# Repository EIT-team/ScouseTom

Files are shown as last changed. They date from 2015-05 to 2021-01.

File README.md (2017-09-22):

# ScouseTom EIT System
The __ScouseTom__ is versatile Electrical Impedance Tomography (EIT) system. It comprises a commercial current source [Keithley 6221](http://www.tek.com/keithley-low-level-sensitive-and-specialty-instruments/keithley-ultra-sensitive-current-sources-seri) and EEG amplifiers e.g. [Biosemi](http://www.biosemi.com/) or the [actiCHamp](http://www.brainvision.com/actichamp.html0), alongside custom switching/control circuitry and software.

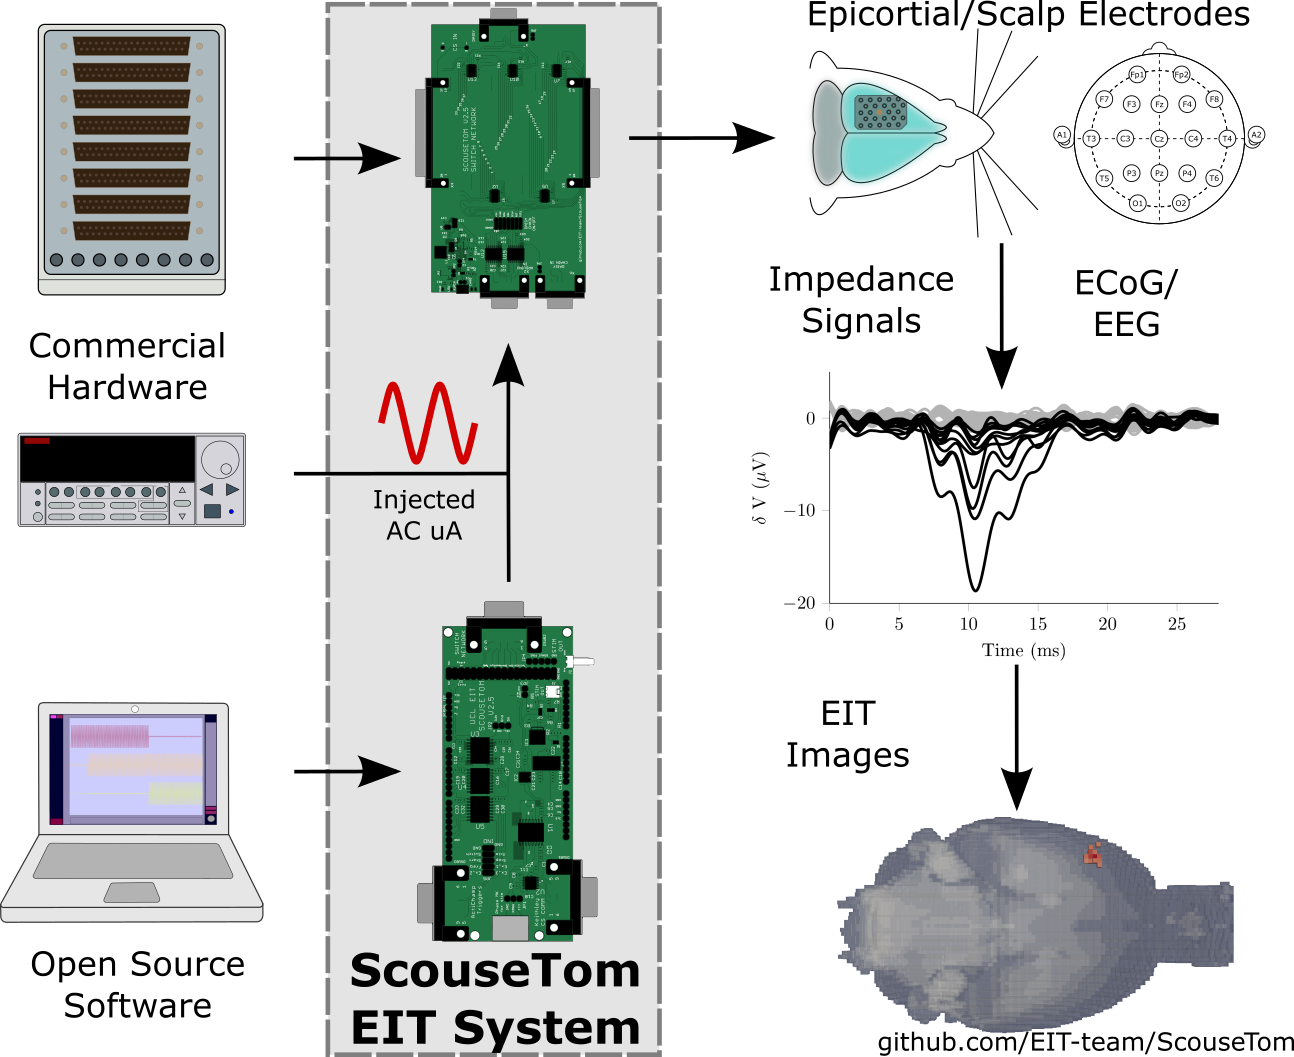
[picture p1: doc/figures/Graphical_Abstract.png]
ScouseTom System Overview


## Making a ScouseTom
If you are interested in making a ScouseTom EIT system, please create an __issue__ in the repo or email us, we would love to help you!

__Checklist__
- [Keithley 6221](http://www.tek.com/keithley-low-level-sensitive-and-specialty-instruments/keithley-ultra-sensitive-current-sources-seri) Current source
- EEG system with sufficient bandwidth. The [Biosemi](http://www.biosemi.com/) and  [actiCHamp](http://www.brainvision.com/actichamp.html0) have been used so far, and likely the [gtec](http://www.gtec.at/) or the [Open-Ephys](http://www.open-ephys.org/) will work too
- Matlab - needed for [processing](https://github.com/EIT-team/Load_data) anyway. Control the system using the Matlab code [here](./src/matlab/)
- [Arduino Due](https://www.arduino.cc/en/Main/arduinoBoardDue) For the controller
- [Arduino Switch Board](./src/schematics/Ard_Shield) This controls the current source and the timing of switching current injection pairs
- [Switch Network](./src/schematics/ScouseTom_SwitchNetwork) At least one, each for 37 channels. This connects the current source to the EEG system and the electrodes

### Citing this work
Please cite the journal article found [here](http://dx.doi.org/10.3390/s17020280)

```
Avery, J., Dowrick, T., Faulkner, M., Goren, N. and Holder, D., 2017.
A Versatile and Reproducible Multi-Frequency Electrical Impedance Tomography System.
Sensors, 17(2), p.280.
```

### Processing the data
To process the data you collect with this system, use the code found in [this repo](https://github.com/EIT-team/Load_data)

### Creating EIT images
Requires a forward model, generated by the code [here](https://github.com/EIT-team/PEITS), and the reconstruction code [here](https://github.com/EIT-team/Reconstruction) to create the images

## Keithley settings
Set on the front panel under `comm`, change `BAUD` to `57.2k` and `Terminator` to `<CR+LF>`

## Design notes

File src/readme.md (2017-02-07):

# ScouseTom Source Files
---

## Arduino
Firmware for the Arduino controllers

## Labview
Measurement of stimulator voltage, used in calibration

## Matlab
PC software for controlling the system via USB

## Schematics
Contains all the schematics in Eagle format for the two PCBs - Arduino Shield, and Switch Network. Also contains resistor phantoms, and other misc. phantoms useful in experiments.

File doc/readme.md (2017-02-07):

# Useful Documentation
This folder contains reference material for hardware, and software used in making the ScouseTom. It also contains 3D models for cases and electrode holders.

- __ActiChamp Holder__ Boxes to hold the active electrodes of the ActiChamp systems
- __Arduino__ Reference for pinouts etc. for Uno and Due
- __BioSemi__ BioSemi Active Two Reference material and software
- __case__ 3D printable cases for both ScouseTom boards - the arduino+shield, and the switch boards
- __Eagle__ Design Rule checks and Cam jobs for EagleCad
- __figures__ Figures of ScouseTom components, useful for Documentation
- __Keithley__ Manuals for Keithley 6221 Current source, as well as guide to upgrading firmware
- __PCB__ Example BOM etc. for ordering boards

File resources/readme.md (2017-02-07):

# Example files

## data
Data collected on resistor phantoms, used for getting system specs for paper.

## protocols
Protocol files which can be used for creating the `ExpSetup` structure

## stim_calibration
Example outputs from stimulator calibration - potentiometer settings for given stimulator voltages. These are the ones used to create the default settings (no one calibrates it anyways...)

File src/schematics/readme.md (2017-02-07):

# Schematics
The schematics needed to create a ScouseTom system and custom electrode boards are all here. All files were created in Eaglecad, and the gerber files are also saved. Where relevant, BOM and pick and place data are included.

- __ _Superseded __ - Old files of historical interest
- __Ard Shield__ - Shield for the Arduino Due which controls the ScouseTom System
- __Debug_Phantom__ A simple resistor phantom, used to quickly check the system is functional, as opposed to calibration
- __Dsub_Croc_Connector__ A breakout for a 37-Way Dsub connector to make it easy to solder crocdile clips to it - to connect to tanks etc.
- __Flexible_Electrode_Connector__ Connector blocks for the flexible electrodes used in epicortical studies
- __Mayo_Phantom__ Resistor Phantom matching epicortical voltages, with three switchable impedances. Used to compare hardware for EP studies
- __Parallel_CS__ Simple current source
- __ScouseTom_SwitchNetwork__ Switch network used in ScouseTom system - 37 channels, and can be daisy chained

## The ones you need to  make a ScouseTom System

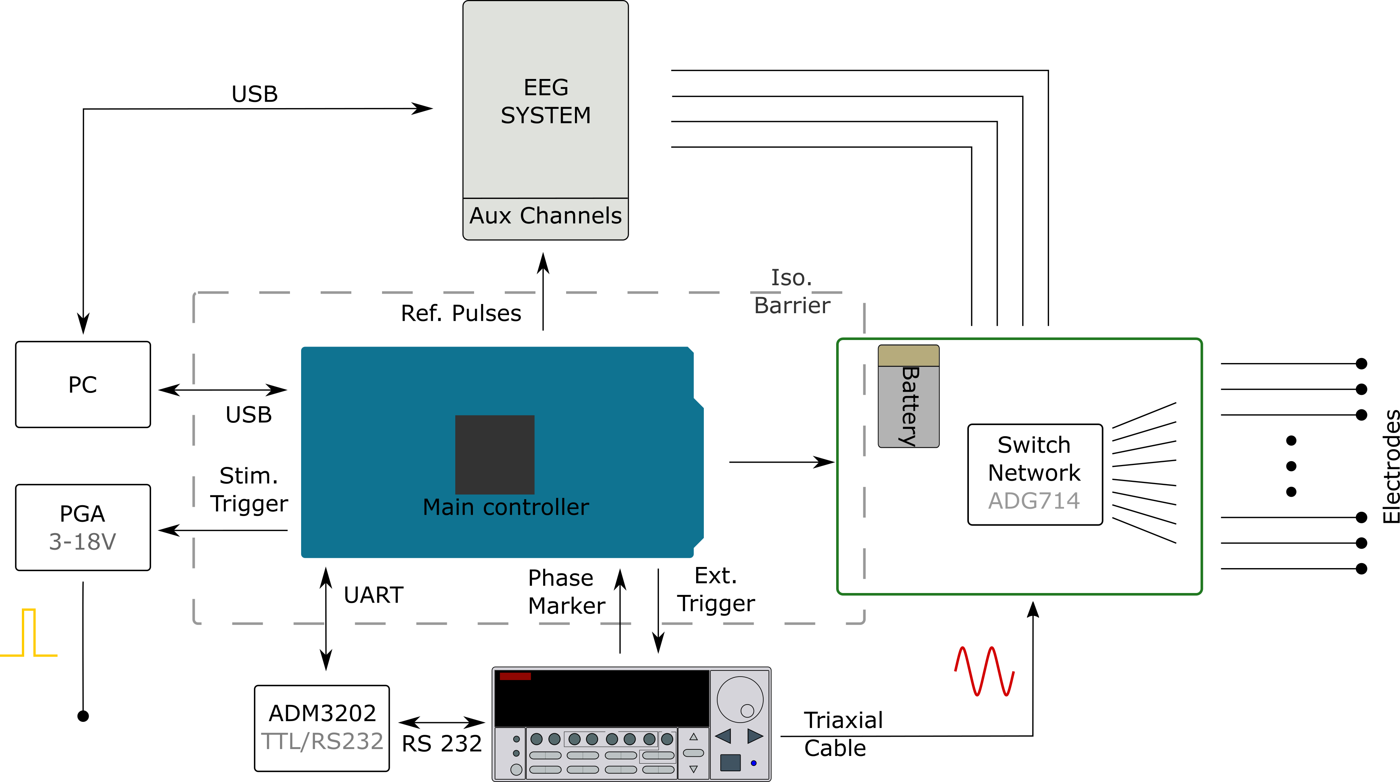
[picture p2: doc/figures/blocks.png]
ScouseTom System blocks


The two boards you will need are __Ard Shield__ and at least one __ScouseTom_SwitchNetwork__. The [wiki page](https://github.com/EIT-team/ScouseTom/wiki/Building-ScouseTom-Boards) has some useful background for what parts require hand soldering.

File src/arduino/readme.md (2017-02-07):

# Arduino Firmware
---
## Arduino Versions
Uses the `Arduino SAM` library, so ensure you have that installed under `boards manager` in the arduino IDE (if you are using that). Set the __Board__ to `Arduino Due (Programming Port)`

## Platformio - compile and upload in command line
We use the tool [Platformio](http://platformio.org/get-started) as you can use it with jenkins easier. Plus you can compile libraries easier. Make sure this is up to date with
```
platformio update
platformio upgrade
```

## ScouseTom Controller
The most important project is `ScouseTom_Control`, which is the firmware necessary to use the system for EIT recordings.

### Other Projects

- __FreqSweep__ Simple code which injects performs a frequency sweep at constant amplitude, with a reference pulse when switching
- __MultiStim__ Controller for two ADG426 switches for higher voltages
- __PulseOutCalibrate__ Code to generate calibration curve for stimulator voltage

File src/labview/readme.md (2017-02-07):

# Stimulator Calibration
This labview code measures the output from the Vstim pin, for a range of potentiometer values. From this it is possible to obtain a calibration curve, `VstimCal.mat` in the `resources` folder. The matlab software uses these values to convert the user desired voltage 3-10V to an 8bit value for the pot.

Run this code in conjunction with the arduino code `PulseOutCalibrate`.

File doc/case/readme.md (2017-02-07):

# 3D Printable cases for ScouseTom Boards
As the size of the boards are a bit odd, we 3D print the cases for both parts of the system. The solid models are included, but those who just want to print can use the `.stl` files:

### Switchboard cases
Print both with the flattest surface at the bottom
- `SwitchBoardCase - Lid`
- `SwitchBoardCase - Main`

### Arduino + Shield cases
To reduce the support material when printing with Makerbot Replicator 2 - use the settings shown in `ScouseTomShieldPrintSettings`

- `ScouseTomCasePrintLid`
- `ScouseTomCasePrintMain`

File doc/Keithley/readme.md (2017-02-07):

# KEITHLEY FIRMWARE

Version should be `D03` for external triggering to work, as Mayo was using for Sana's epilepsy stuff.

Use the flashwizard on windows 7 only! Already installed on HPZbook
Use ethernet cable as USB/Serial connector didnt work. Change Keithley to `ethernet comm` mode on front panel. Change on PC wired adaptor IPv4 settings: subnet mask and default gateway to match those on keithley.

Win

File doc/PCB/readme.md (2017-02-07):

# PCB Documentation
We have been using PCBtrain in the UK to make the boards, this folder contains info regarding the free components they offer, and example BOM and Pick and Place data we send to them

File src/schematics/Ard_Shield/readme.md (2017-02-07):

# Arduino Shield

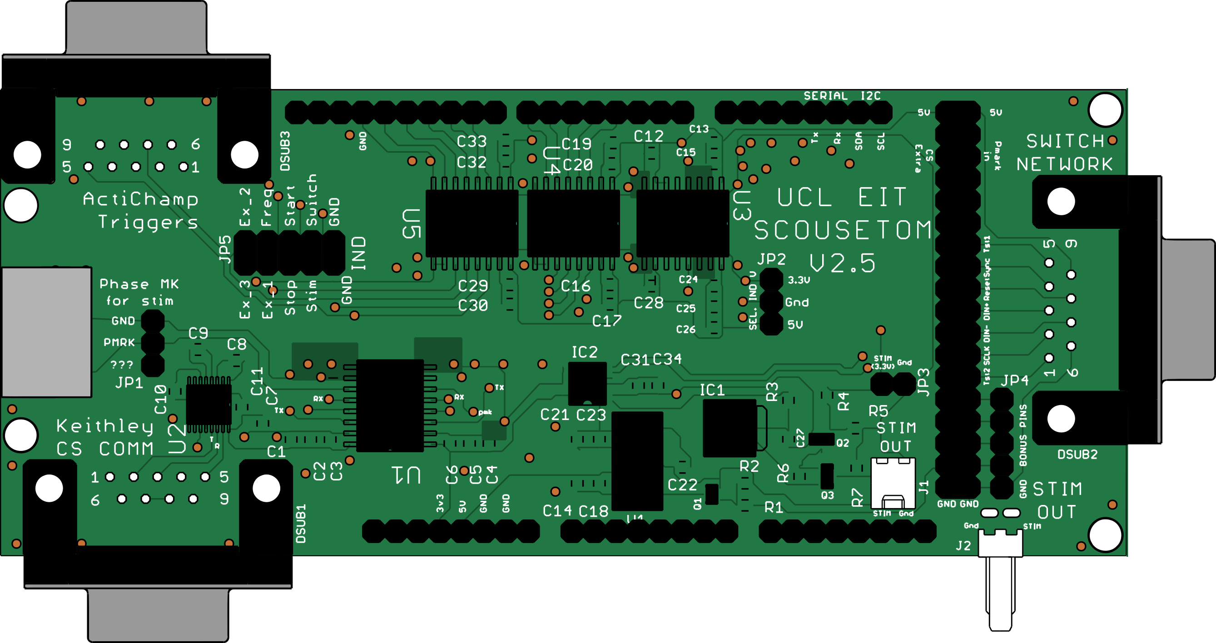
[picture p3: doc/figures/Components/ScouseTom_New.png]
Shield

The Arduino Shield has several functions:

- Communication with PC via USB serial. This is done through the programming port on the Arduinio Due. i.e. `Serial.print` etc. with baud rate 115200
- Communication with Keithley 6221 current source via isolated RS232 port - baud rate 57600 via Serial port `Serial1.print` etc.
- Reference triggers to EEG system. Pulses sent to digital inputs of EEG systems, isolated from Arduino pins
- Control of switch networks. Control signals sent to Switchboard (isolation on the switchboard)
- Stimulation triggers - Based on phase marker of Keithley 6221 - stimulation pulses are randomised with respect to the phase of the injected current.
- Stimulation voltage - the voltage of the pulses can be sent from 3.3 to 12 V. This is useful for controlling the electrical stimulator box  

ScouseTom System blocks

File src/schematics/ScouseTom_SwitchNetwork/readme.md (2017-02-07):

# SwitchBoard

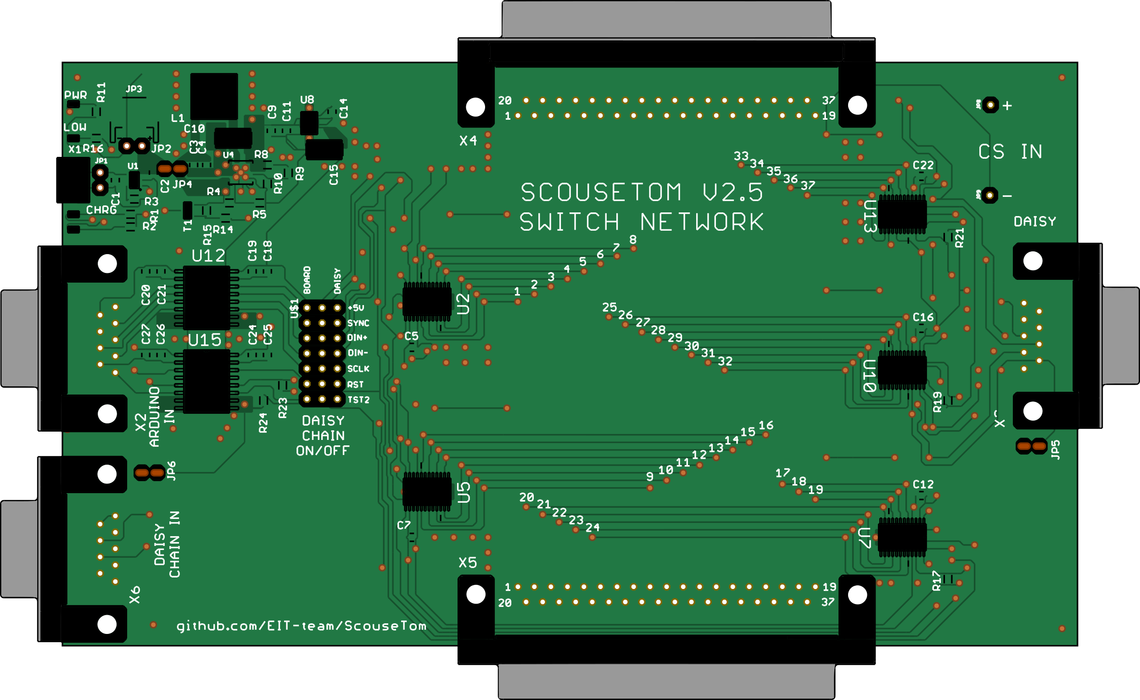
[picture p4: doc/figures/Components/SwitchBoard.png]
SwitchBoard


The switchboard connects the source and sink connections of the Keithley 6221 ( the + and - pins) to any two electrodes out of the 37 connections on the DSub.

### Powering the board
The board is powered by a Lipo battery, and a charging circuit is included.

### Daisy Chaining
The control signals to set the switches come from either the `Arduino in` Dsub9, in which case they pass through the Isolators, or the `Daisy Chain in` Dsub9. These are selected by the jumpers labelled `Daisy Chain ON/OFF`

ScouseTom System blocks

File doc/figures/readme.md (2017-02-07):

# ScouseTom Figures
This folder contains the vector drawings of the components of the system used to make figures like this:

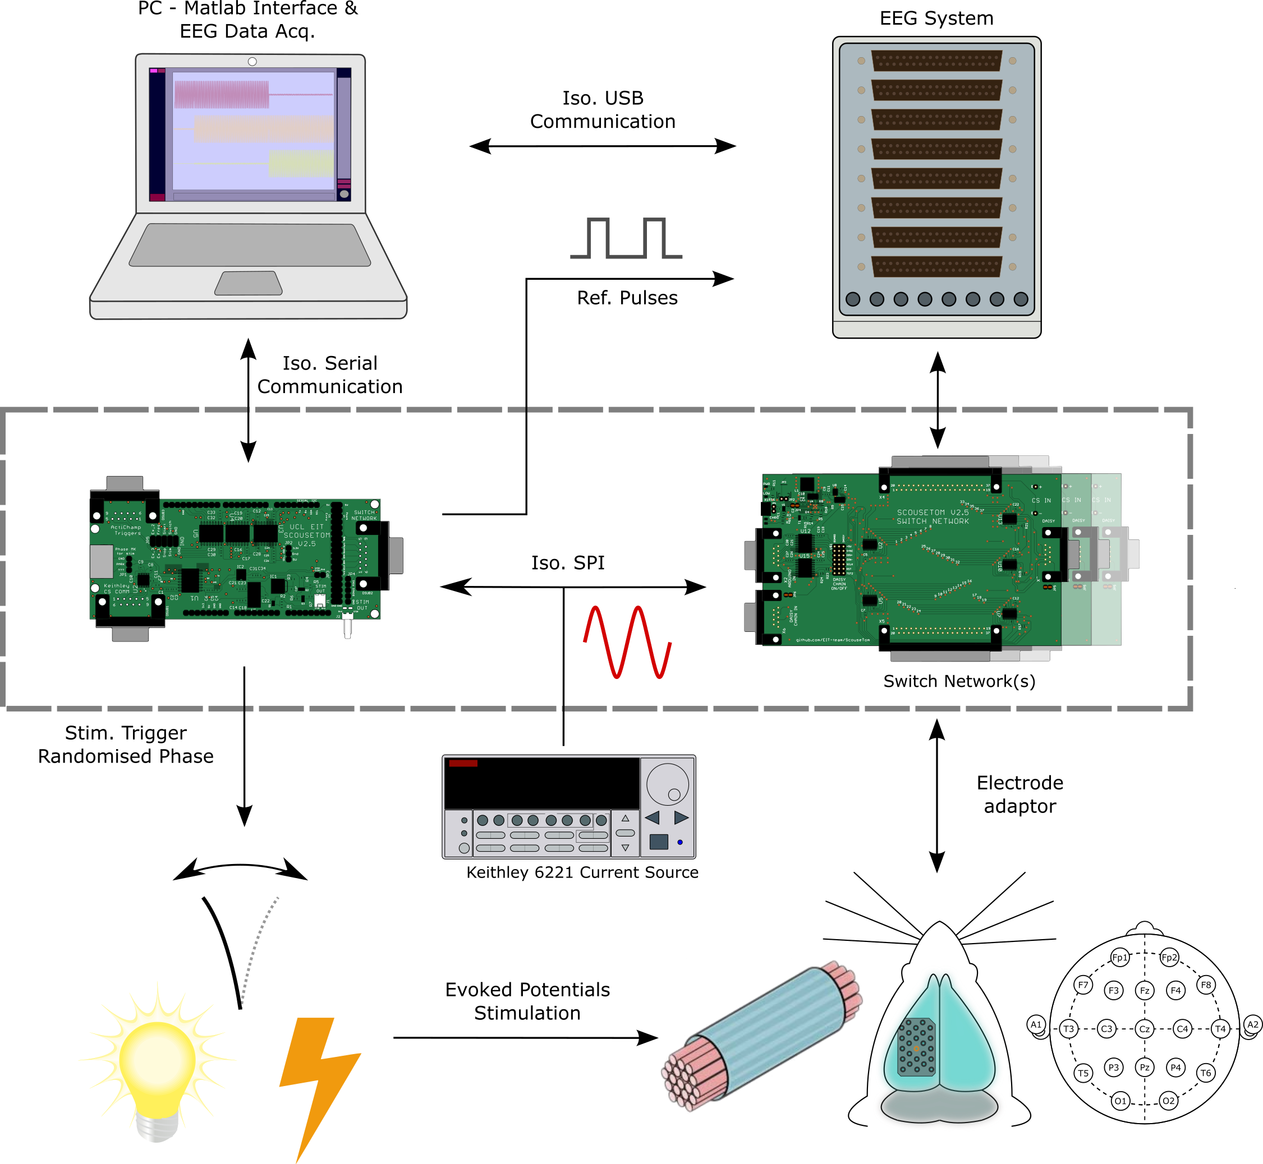
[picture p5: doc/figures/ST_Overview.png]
ScouseTom Overview


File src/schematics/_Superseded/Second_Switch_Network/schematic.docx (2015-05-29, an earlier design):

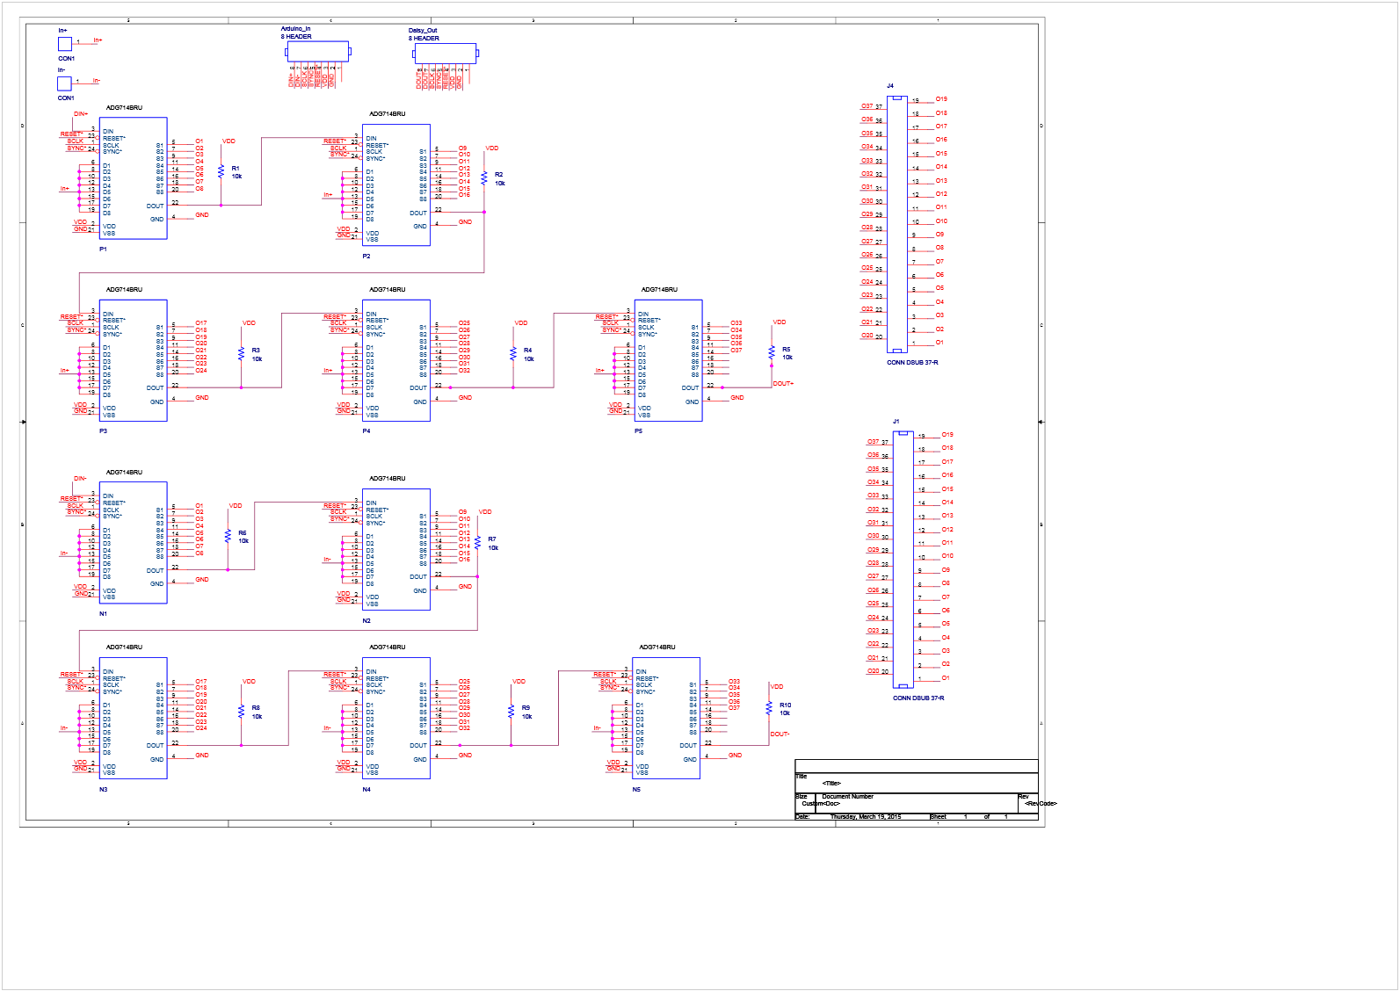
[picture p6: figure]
Machine generated alternative text: 5 5 4 4 3 3 2 2 1 1 D D C C B B A A DIN+ DIN+ DIN- DIN- GND GND GND GND GND GND GND GND In+ In+ In+ In+ In- In- In- In- O1 O1 O1 O10 O10 O10 O11 O11 O11 O12 O12 O12 O13 O13 O13 O14 O14 O14 O15 O15 O15 O16 O16 O16 O17 O17 O17 O18 O18 O18 O19 O19 O19 O2 O2 O2 O20 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

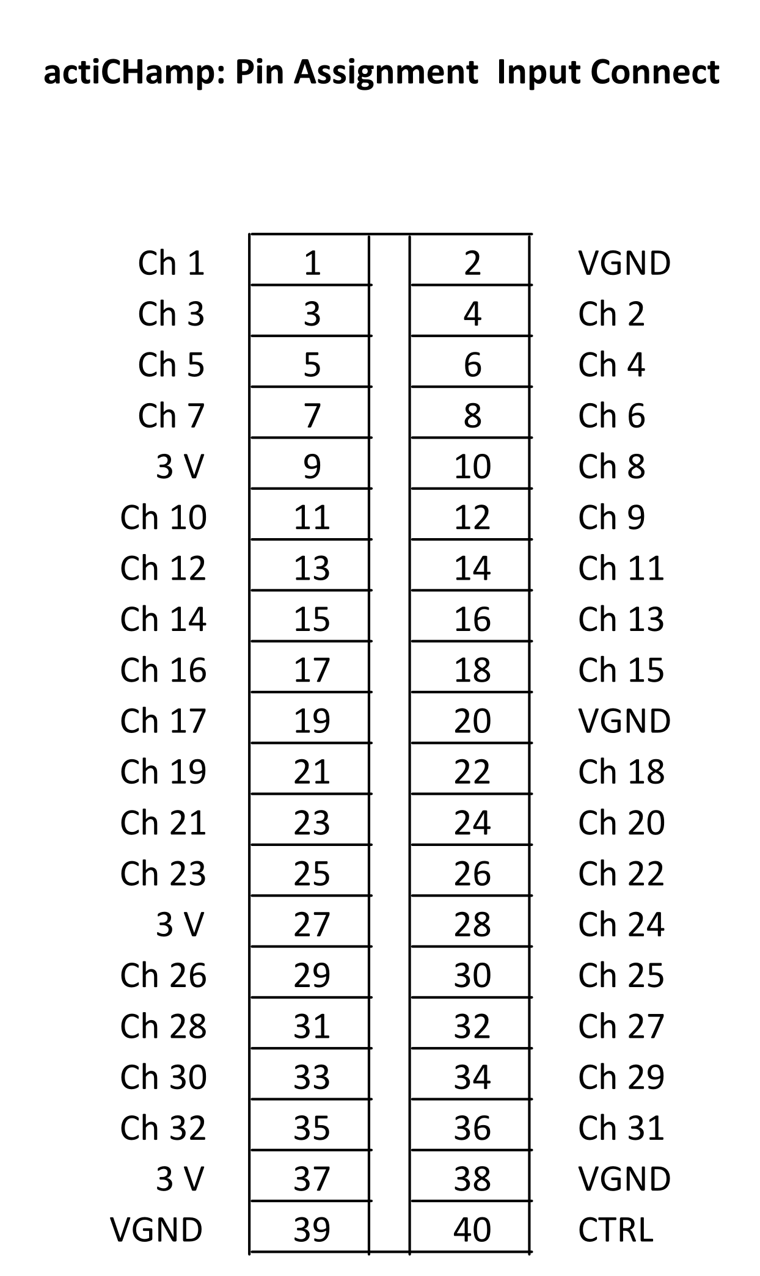
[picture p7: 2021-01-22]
doc/ActiChamp/actiCHamp_InputConnectorPinAssignment.png

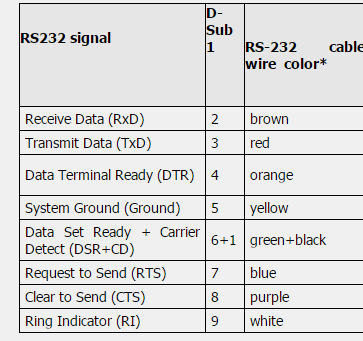
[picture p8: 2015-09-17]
doc/SerialCablePinOuts.png

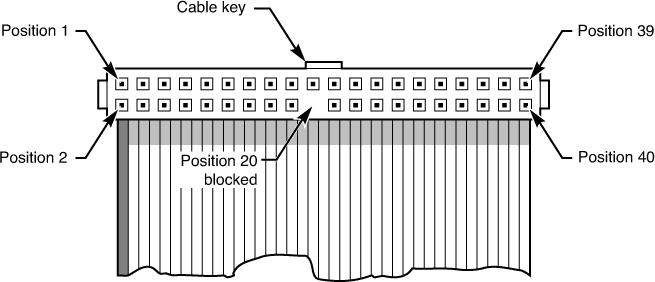
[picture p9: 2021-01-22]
doc/ActiChamp/40-pin socket.jpg

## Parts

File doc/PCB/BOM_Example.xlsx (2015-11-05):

Part | Value | Device | Package | Description | MPN | OC_FARNELL | PCBTRAIN FREE
C1 | 10uF | C-EUC0805 | C0805 | CAPACITOR, European symbol | MC0805X106K6R3CT | 2320852
C2 | 10uF | C-EUC0805 | C0805 | CAPACITOR, European symbol | MC0805X106K6R3CT | 2320852
C3 | 10uF | C-EUC0805 | C0805 | CAPACITOR, European symbol | MC0805X106K6R3CT | 2320852
C4 | 0.1uF | C-EUC0805 | C0805 | CAPACITOR, European symbol | MC0805B104K500CT | 1759265 | PCB Train Free Component Stock
C5 | 0.1uF | C-EUC0805 | C0805 | CAPACITOR, European symbol | MC0805B104K500CT | 1759265 | PCB Train Free Component Stock
C6 | 0.1uF | C-EUC0805 | C0805 | CAPACITOR, European symbol | MC0805B104K500CT | 1759265 | PCB Train Free Component Stock
C7 | 0.1uF | C-EUC0805 | C0805 | CAPACITOR, European symbol | MC0805B104K500CT | 1759265 | PCB Train Free Component Stock
C8 | 0.1uF | C-EUC0805 | C0805 | CAPACITOR, European symbol | MC0805B104K500CT | 1759265 | PCB Train Free Component Stock
C9 | 2.2uF | C-EUC0805 | C0805 | CAPACITOR, European symbol | MC0805B225K250CT | 2320829 | PCB Train Free Component Stock
C10 | 100uF | CPOL-EUCT6032 | CT6032 | POLARIZED CAPACITOR, European symbol | 293D107X9010C2TE3 | 2353063
C11 | 10uF | C-EUC0805 | C0805 | CAPACITOR, European symbol | MC0805X106K6R3CT | 2320852
C12 | 0.1uF | C-EUC0805 | C0805 | CAPACITOR, European symbol | MC0805B104K500CT | 1759265 | PCB Train Free Component Stock
C13 | 0.1uF | C-EUC0805 | C0805 | CAPACITOR, European symbol | MC0805B104K500CT | 1759265 | PCB Train Free Component Stock
C14 | 0.01uF | C-EUC0805 | C0805 | CAPACITOR, European symbol | MC0805B103K500CT | 1759246 | PCB Train Free Component Stock
C15 | 100uF | CPOL-EUCT6032 | CT6032 | POLARIZED CAPACITOR, European symbol | 293D107X9010C2TE3 | 2353063
C16 | 0.1uF | C-EUC0805 | C0805 | CAPACITOR, European symbol | MC0805B104K500CT | 1759265 | PCB Train Free Component Stock
C17 | 0.1uF | C-EUC0805 | C0805 | CAPACITOR, European symbol | MC0805B104K500CT | 1759265 | PCB Train Free Component Stock
C18 | .1uF | C-EUC0805 | C0805 | CAPACITOR, European symbol | MC0805B104K500CT | 1759265 | PCB Train Free Component Stock
C19 | 1uF | C-EUC0805 | C0805 | CAPACITOR, European symbol | MC0805B105K250CT | 2320827 | PCB Train Free Component Stock
C20 | .1uF | C-EUC0805 | C0805 | CAPACITOR, European symbol | MC0805B104K500CT | 1759265 | PCB Train Free Component Stock
C21 | 1uF | C-EUC0805 | C0805 | CAPACITOR, European symbol | MC0805B105K250CT | 2320827 | PCB Train Free Component Stock
C22 | 0.1uF | C-EUC0805 | C0805 | CAPACITOR, European symbol | MC0805B104K500CT | 1759265 | PCB Train Free Component Stock
C23 | 0.1uF | C-EUC0805 | C0805 | CAPACITOR, European symbol | MC0805B104K500CT | 1759265 | PCB Train Free Component Stock
C24 | .1uF | C-EUC0805 | C0805 | CAPACITOR, European symbol | MC0805B104K500CT | 1759265 | PCB Train Free Component Stock
C25 | 1uF | C-EUC0805 | C0805 | CAPACITOR, European symbol | MC0805B105K250CT | 2320827 | PCB Train Free Component Stock
C26 | .1uF | C-EUC0805 | C0805 | CAPACITOR, European symbol | MC0805B104K500CT | 1759265 | PCB Train Free Component Stock
C27 | 1uF | C-EUC0805 | C0805 | CAPACITOR, European symbol | MC0805B105K250CT | 2320827 | PCB Train Free Component Stock
L1 | 6.8uH | WE-PD-7447779006_7332/7345_PLASTIC_BASE | WE-PD_7332/7345_PLASTIC_BASE | SMD-Shielded Power Inductors WE-PD | LT1763CDE-5 | 1556468
LED1 | YELLOW | LEDSML0805 | SML0805 | LED | KPT-2012YC | 2099243 | PCB Train Free Component Stock
LED2 | GREEN | LEDSML0805 | SML0805 | LED | KPT-2012CGCK | 2099235 | PCB Train Free Component Stock
LED3 | GREEN | LEDSML0805 | SML0805 | LED | KPT-2012CGCK | 2099235 | PCB Train Free Component Stock
LED4 | RED | LEDSML0805 | SML0805 | LED | KPT-2012EC | 2099236 | PCB Train Free Component Stock
R1 | 470 | R-EU_M0805 | M0805 | RESISTOR, European symbol | MC01W08051470R | 2129087 | PCB Train Free Component Stock
R2 | 1k | R-EU_M0805 | M0805 | RESISTOR, European symbol | MC01W080511K | 2129113 | PCB Train Free Component Stock
R3 | 2k | R-EU_M0805 | M0805 | RESISTOR, European symbol | MC01W080512K | 2129135 | PCB Train Free Component Stock
R4 | 2M | R-EU_M0805 | M0805 | RESISTOR, European symbol | MC01W080512M00 | 2129375 | PCB Train Free Component Stock
R5 | 360k | R-EU_M0805 | M0805 | RESISTOR, European symbol | MC01W08051360K | 2129319 | PCB Train Free Component Stock
R6 | 10k | R-EU_M0805 | M0805 | RESISTOR, European symbol | MC01W0805110K | 9332391 | PCB Train Free Component Stock
R7 | 10k | R-EU_M0805 | M0805 | RESISTOR, European symbol | MC01W0805110K | 9332391 | PCB Train Free Component Stock
R8 | 1.8M | R-EU_M0805 | M0805 | RESISTOR, European symbol | MC01W080511M80 | 2129372 | PCB Train Free Component Stock
R9 | 82k | R-EU_M0805 | M0805 | RESISTOR, European symbol | MC01W08051820K | 2351393 | PCB Train Free Component Stock
R10 | 200k | R-EU_M0805 | M0805 | RESISTOR, European symbol | MC01W080512M00 | 2129375 | PCB Train Free Component Stock
R11 | 1k | R-EU_M0805 | M0805 | RESISTOR, European symbol | MC01W080511K | 2129113 | PCB Train Free Component Stock
R12 | 10k | R-EU_M0805 | M0805 | RESISTOR, European symbol | MC01W0805110K | 9332391 | PCB Train Free Component Stock
R13 | 10k | R-EU_M0805 | M0805 | RESISTOR, European symbol | MC01W0805110K | 9332391 | PCB Train Free Component Stock
R14 | 4.7k | R-EU_M0805 | M0805 | RESISTOR, European symbol | MC01W0805147K | 2129250 | PCB Train Free Component Stock
R15 | 47k | R-EU_M0805 | M0805 | RESISTOR, European symbol | MC01W08051470K | 2129329 | PCB Train Free Component Stock
R16 | 1k | R-EU_M0805 | M0805 | RESISTOR, European symbol | MC01W080511K | 2129113 | PCB Train Free Component Stock
R17 | 10k | R-EU_M0805 | M0805 | RESISTOR, European symbol | MC01W0805110K | 9332391 | PCB Train Free Component Stock
R18 | 10k | R-EU_M0805 | M0805 | RESISTOR, European symbol | MC01W0805110K | 9332391 | PCB Train Free Component Stock
R19 | 10k | R-EU_M0805 | M0805 | RESISTOR, European symbol | MC01W0805110K | 9332391 | PCB Train Free Component Stock
R20 | 10k | R-EU_M0805 | M0805 | RESISTOR, European symbol | MC01W0805110K | 9332391 | PCB Train Free Component Stock
R21 | 10k | R-EU_M0805 | M0805 | RESISTOR, European symbol | MC01W0805110K | 9332391 | PCB Train Free Component Stock
R22 | 10k | R-EU_M0805 | M0805 | RESISTOR, European symbol | MC01W0805110K | 9332391 | PCB Train Free Component Stock
R23 | 10M | R-EU_M0805 | M0805 | RESISTOR, European symbol | MC01W0805110M0 | 2129417 | PCB Train Free Component Stock
R24 | 10M | R-EU_M0805 | M0805 | RESISTOR, European symbol | MC01W0805110M0 | 2129417 | PCB Train Free Component Stock
T1 | PNP | BC807-40-PNP-SOT23-BEC | SOT23-BEC | PNP Transistror | BC807-40,215 | 2336778 | PCB Train Free Component Stock
U1 | MCP73831 | MCP73831 | SOT23-5 | Miniature single cell, fully integrated Li-Ion, Li-polymer charge management controller | MCP73831T-2ACI/OT | 1332158
U2 | ADG714BRUZ | ADG714BRUZ | SOP65P640X120-24N | CMOS, Low Voltage Serially Controlled, Octal SPST Switches | ADG714BRUZ | 9604367
U3 | ADG714BRUZ | ADG714BRUZ | SOP65P640X120-24N | CMOS, Low Voltage Serially Controlled, Octal SPST Switches | ADG714BRUZ | 9604367
U4 | TPS61090RSAR | VREG_TPS6103XSPARKFUNVERSION | QFN16-4X4 | TPS6103x 4A Boost - 1.8-5.5V Input, Adjustable Output to 5.5V | TPS61090RSARG4 | 1207334
U5 | ADG714BRUZ | ADG714BRUZ | SOP65P640X120-24N | CMOS, Low Voltage Serially Controlled, Octal SPST Switches | ADG714BRUZ | 9604367
U6 | ADG714BRUZ | ADG714BRUZ | SOP65P640X120-24N | CMOS, Low Voltage Serially Controlled, Octal SPST Switches | ADG714BRUZ | 9604367
U7 | ADG714BRUZ | ADG714BRUZ | SOP65P640X120-24N | CMOS, Low Voltage Serially Controlled, Octal SPST Switches | ADG714BRUZ | 9604367
U8 | LT1763CDE-5 | LT1763CDE-5 | DFN12 | 500mA, Low Noise, LDO Micropower Regulators | LT1763CDE-5 | 1556468
U9 | ADG714BRUZ | ADG714BRUZ | SOP65P640X120-24N | CMOS, Low Voltage Serially Controlled, Octal SPST Switches | ADG714BRUZ | 9604367
U10 | ADG714BRUZ | ADG714BRUZ | SOP65P640X120-24N | CMOS, Low Voltage Serially Controlled, Octal SPST Switches | ADG714BRUZ | 9604367
U11 | ADG714BRUZ | ADG714BRUZ | SOP65P640X120-24N | CMOS, Low Voltage Serially Controlled, Octal SPST Switches | ADG714BRUZ | 9604367
U12 | ADUM1410ARWZ | ADUM1410ARWZ | SOIC127P1032X265-16N | ISOLATOR, DGTL, 4CHAN | ADUM1410ARWZ | 2067770
U13 | ADG714BRUZ | ADG714BRUZ | SOP65P640X120-24N | CMOS, Low Voltage Serially Controlled, Octal SPST Switches | ADG714BRUZ | 9604367
U14 | ADG714BRUZ | ADG714BRUZ | SOP65P640X120-24N | CMOS, Low Voltage Serially Controlled, Octal SPST Switches | ADG714BRUZ | 9604367
U15 | ADUM1412ARWZ | ADUM1412ARWZ | SOIC127P1032X265-16N | IC, DIG ISOLATOR | ADUM1412ARWZ | 2377152
X1 | USB-MICROB | USB-MICROB | USB-MICROB | USB Connectors | USB3070-30-A | 2293836
 |  |  | Number unique components | 28
 |  |  | Number Free | 50
 |  |  | Number Non Free | 23
 |  |  | Total | 73

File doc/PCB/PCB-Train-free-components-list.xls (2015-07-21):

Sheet: Free Capacitors
CATEGORY | Farads | Description from Farnell | Package | MANUFACTURER | MFR PART NO. | SUPPLIER | SUPPLIER PART NO. | Power | Tolerance | Notes | Value
CAPACITOR | 1e-12 | CAP, MLCC, C0G/NP0, 1PF, 50V, 0402 | 0402 | Multicomp | MCCA000081 | Farnell | 1758930 | 50V | +/-2.5pf | NP0 | 1PF
CAPACITOR | 1e-12 | CAP, MLCC, C0G/NP0, 1PF, 50V, 0603 | 0603 | Multicomp | MCCA000182 | Farnell | 1759041 | 50V | +/-2.5pf | NP0 | 1PF
CAPACITOR | 1e-12 | CAP, MLCC, C0G/NP0, 1PF, 50V, 0805 | 0805 | MULTICOMP | MCCA000308 | Farnell | 1759179 | 50V | +/-0.25PF | NPO | 1PF
CAPACITOR | 1.5e-12 | CAP, MLCC,C0G/NP0,1.5PF,50V,0603 | 0603 | Multicomp | MCCA000183 | Farnell | 1759042 | 50V | +/-2.5pf | NP0 | 1.5PF
CAPACITOR | 1.5e-12 | CAP, MLCC,C0G/NP0,1.5PF,50V,0805 | 0805 | Multicomp | MCCA000309 | Farnell | 1759180 | 50V | +/-2.5pf | NP0 | 1.5PF
CAPACITOR | 2.2e-12 | CAP, MLCC, C0G/NP0, 2.2PF, 50V, 0402 | 0402 | Yaego (Phycomp) | CC0402CRNPO9BN2R2 | Farnell | 3019123 | 50V | +/-2.5pf | NP0 | 2.2PF
CAPACITOR | 2.2e-12 | CAP, MLCC, C0G/NP0, 2.2PF, 50V, 0603 | 0603 | Multicomp | MCCA000979 | Farnell | 1856138 | 50V | +/-2.5pf | NP0 | 2.2PF
CAPACITOR | 2.2e-12 | CAP, MLCC, C0G/NP0, 2.2PF, 200V, 0805 | 0805 | Multicomp | MCCA000651 | Farnell | 1855759 | 50V | 5% | NP0 | 2.2PF
CAPACITOR | 2.7e-12 | CAP, MLCC, C0G/NP0, 2.7PF, 50V, 0805 | 0805 | AVX | 08055A2R7CAT2A | Farnell | 2332766 | 50V | 5% | NP0 | 2.7PF
CAPACITOR | 3.3e-12 | CAP, MLCC, C0G/NP0, 3.3PF, 50V, 0603 | 0603 | MURATA | GRM1885C1H3R3CZ01D | Farnell | 8819785 | 50V | 7% | NP0 | 3.3PF
CAPACITOR | 3.3e-12 | CAP, MLCC, C0G/NP0, 3.3PF, 50V, 0805 | 0805 | AVX | 08055A3R3CAT2A | Farnell | 2332770 | 50V | +/-0.25PF | NP0 | 3.3PF
CAPACITOR | 3.3e-12 | CAP, MLCC, C0G/NP0, 3.3PF, 50V, 1206 | 1206 | KEMET | C1206C339C5GACTU | Farnell | 1650901 | 50V | +/-0.25PF | NP0 | 3.3PF
CAPACITOR | 3.9e-12 | CAP, MLCC, C0G/NP0, 3.9PF, 50V, 0402 | 0402 | Murata | GRM1555C1H3R9CA01D | Farnell | 1828871 | 50V | +/-2.5pf | NP0 | 3.9PF
CAPACITOR | 3.9e-12 | CAP, MLCC, C0G/NP0, 3.9PF, 50V, 0603 | 0603 | YAGEO (PHYCOMP) | CC0603CRNPO9BN3R9 | Farnell | 721918 | 50V | +/-0.25PF | NP0 | 3.0PF
CAPACITOR | 4.7e-12 | CAP, MLCC, C0G/NP0, 6.8PF, 100V, 0805 | 0805 | Multicomp | MCCA001090 | Farnell | 1856262 | 50V | +/-2.5pf | NP0 | 4.7PF
CAPACITOR | 4.7e-12 | CAP, MLCC, C0G/NP0, 4.7PF, 50V, 0402 | 0402 | Yaego (Phycomp) | CC0402CRNPO9BN4R7 | Farnell | 3019147 | 50V | +/-2.5pf | NP0 | 4.7PF
CAPACITOR | 4.7e-12 | CAP CERAM, COG, 4.7PF, 50V, 0603 | 0603 | TDK | C1608C0G1H4R7C | Farnell | 1844187 | 50V | +/-2.5pf | NP0 | 4.7PF
CAPACITOR | 5.6e-12 | CAP, MLCC, C0G/NP0, 5.6PF, 50V, 0402 | 0402 | Murata | GRM1555C1H5R6CA01D | Farnell | 1828872 | 50V | +/-2.5pf | NP0 | 5.6PF
CAPACITOR | 5.6e-12 | CAP, MLCC, C0G/NP0, 5.6PF, 50V,0603 | 0603 | Yageo (Phycomp) | CC0603DRNPO9BN5R6 | Farnell | 1362464 | 50V | +/-0.5PF | NP0 | 5.6PF
CAPACITOR | 6.8e-12 | CAP, MLCC, C0G/NP0, 6.8PF, 50V, 0603 | 0603 | MULTICOMP | MCCA000982 | Farnell | 1856141 | 50V | +/-0.25PF | COG | 6.8PF
CAPACITOR | 8.2e-12 | CAP, MLCC, C0G/NP0, 8.2PF, 50V, 0603 | 0603 | Kemet | C0603C829J5GACAUTO | Farnell | 2070432 | 50V | 5% | NP0 | 8.2PF
CAPACITOR | 8.2e-12 | CAP CERAM, COG, 8.2PF 50V,1206 | 1206 | KEMET | C1206C829D5GACTU | Farnell | 1164024 | 50V | +/-0.5PF | COG | 8.2PF
CAPACITOR | 1e-11 | CAP, MLCC, C0G/NP0, 10PF, 50V, 0402 | 0402 | Multicomp | MC0402N100J500CT | Farnell | 2320761 | 50V | 5% | NP0 | 10PF
CAPACITOR | 1e-11 | CAP, MLCC, C0G/NP0, 10PF, 50V, 0603 | 0603 | Multicomp | MC0603N100J500CT | Farnell | 2320799 | 50V | 5% | NP0 | 10PF
CAPACITOR | 1e-11 | CAP, MLCC, C0G/NP0, 10PF, 50V, 0805 | 0805 | Multicomp | MC0805N100J500CT | Farnell | 2320834 | 50V | 5% | NP0 | 10PF
CAPACITOR | 1e-11 | CAP, MLCC, C0G/NP0, 10PF, 50V, 1206 | 1206 | AVX | 12065A100JAT2A | Farnell | 2280690 | 50V | 5% | NP0 | 10pF
CAPACITOR | 1.2e-11 | CAP, MLCC, C0G/NP0, 12PF, 50V, 0402 | 0402 | Multicomp | MC0402N120J500CT | Farnell | 1758943 | 50V | 5% | NP0 | 12PF
CAPACITOR | 1.2e-11 | CAP, MLCC, C0G/NP0, 12PF, 50V, 0603 | 0603 | Multicomp | MC0603N120J500CT | Farnell | 1759054 | 50V | 5% | NP0 | 12PF
CAPACITOR | 1.2e-11 | CAP, MLCC, C0G/NP0, 12PF, 50V, 0805 | 0805 | Multicomp | MC0805N120J500CT | Farnell | 1759192 | 50V | 5% | NP0 | 12PF
CAPACITOR | 1.5e-11 | CAP, MLCC, C0G/NP0, 15PF,50V,0603 | 0603 | Multicomp | MC0603N150J500CT | Farnell | 1759055 | 50V | 5% | NP0 | 15PF
CAPACITOR | 1.5e-11 | CAP, MLCC, C0G/NP0, 15PF, 50V, 0805 | 0805 | Multicomp | MC0805N150J500CT | Farnell | 1759193 | 50V | 5% | NP0 | 15PF
CAPACITOR | 1.5e-11 | CAP, MLCC, C0G/NP0, 15PF,50V,1206 | 1206 | Kemet | C1206C150J5GACTU | Farnell | 1800827 | 50V | 5% | NP0 | 15PF
CAPACITOR | 1.8e-11 | CAP, MLCC, C0G/NP0, 18PF, 50V, 0402 | 0402 | Multicomp | MC0402N180J500CT | Farnell | 1758947 | 50V | 5% | NP0 | 18PF
CAPACITOR | 1.8e-11 | CAP, MLCC, C0G/NP0, 18PF, 50V, 0603 | 0603 | Multicomp | MC0603N180J500CT | Farnell | 1759056 | 50V | 5% | NP0 | 18PF
CAPACITOR | 1.8e-11 | CAP, MLCC, C0G/NP0, 18PF, 50V, 0805 | 0805 | Multicomp | MC0805N180J500CT | Farnell | 1759194 | 50V | 5% | NP0 | 18PF
CAPACITOR | 1.8e-11 | CAP, MLCC, C0G/NP0, 18PF, 50V, 1206 | 1206 | Kemet | C1206C180J5GACTU | Farnell | 1650895 | 50V | 5% | NP0 | 18PF
CAPACITOR | 2e-11 | CAP, MLCC, C0G/NP0, 20PF, 50V, 0402 | 0402 | Multicomp | MC0402N200J500CT | Farnell | 1758948 | 50V | 5% | NP0 | 20PF
CAPACITOR | 2e-11 | CAP, MLCC, C0G/NP0, 20PF, 50V, 0603 | 0603 | Kemet | C0603C200J5GACTU | Farnell | 1865475 | 50V | 5% | C0G | 20PF
CAPACITOR | 2.2e-11 | CAP, MLCC, C0G/NP0, 22PF, 50V, 0402 | 0402 | Multicomp | MC0402N220J500CT | Farnell | 1758951 | 50V | 5% | NP0 | 22PF
CAPACITOR | 2.2e-11 | CAP, MLCC, C0G/NP0, 22PF, 50V, 0603 | 0603 | Multicomp | MC0603N220J500CT | Farnell | 1759057 | 50V | 5% | NP0 | 22PF
CAPACITOR | 2.2e-11 | CAP, MLCC, C0G/NP0, 22PF, 50V, 0805 | 0805 | Multicomp | MC0805N220J500CT | Farnell | 1759195 | 50V | 5% | NP0 | 22PF
CAPACITOR | 2.2e-11 | CAP, MLCC, C0G/NP0, 22PF, 50V, 1206 | 1206 | Multicomp | MC1206N220J500CT | Farnell | 2320891 | 50V | 5% | NP0 | 22PF
CAPACITOR | 2.7e-11 | CAP, MLCC, C0G/NP0, 27PF, 50V, 0805 | 0805 | Multicomp | MC0805N270J500CT | Farnell | 1759196 | 50V | 5% | NP0 | 27PF
CAPACITOR | 3e-11 | CAPACITOR, MLCC, 0805, 100V, 30PF | 0805 | AVX | 08051A300JAT2A | Farnell | 1740653 | 100V | 5% |  | 30PF
CAPACITOR | 3.3e-11 | CAP, MLCC, C0G/NP0, 33PF, 50V, 0402 | 0402 | Multicomp | MC0402N330J500CT | Farnell | 1758955 | 50V | 5% | NP0 | 33PF
CAPACITOR | 3.3e-11 | CAP, MLCC, C0G/NP0, 33PF, 50V, 0603 | 0603 | Multicomp | MC0603N330J500CT | Farnell | 1759059 | 50V | 5% | NP0 | 33PF
CAPACITOR | 3.3e-11 | CAP, MLCC, C0G/NP0, 33PF, 50V, 0805 | 0805 | Multicomp | MC0805N330J500CT | Farnell | 1759197 | 50V | 5% | NP0 | 33PF
CAPACITOR | 3.3e-11 | CAP, MLCC, C0G/NP0, 33PF, 50V, 1206 | 1206 | Multicomp | MC1206N330J500CT | Farnell | 2320894 | 50V | 5% | NP0 | 33PF
CAPACITOR | 3.9e-11 | CAP CERAM, COG, 39PF 50V, 0402 | 0402 | MULTICOMP | MC0402N390K500CT | Farnell | 1709848 | 50V | 10% | COG | 39PF
CAPACITOR | 3.9e-11 | CAP, MLCC, C0G/NP0, 39PF, 50V, 0603 | 0603 | Multicomp | MC0603N390J500CT | Farnell | 1759060 | 50V | 5% | NP0 | 39PF
CAPACITOR | 4.7e-11 | CAP, MLCC, C0G/NP0, 47PF, 50V, 0402 | 0402 | Multicomp | MC0402N470J500CT | Farnell | 1758959 | 50V | 5% | NP0 | 47PF
CAPACITOR | 4.7e-11 | CAP, MLCC, C0G/NP0, 47PF, 50V, 0603 | 0603 | Multicomp | MC0603N470J500CT | Farnell | 1759062 | 50V | 5% | NP0 | 47PF
CAPACITOR | 4.7e-11 | CAP, MLCC, C0G/NP0, 47PF, 50V, 0805 | 0805 | Multicomp | MC0805N470J500CT | Farnell | 1759199 | 50V | 5% | NP0 | 47PF
CAPACITOR | 4.7e-11 | CAP, MLCC, C0G/NP0, 47PF, 50V, 1206 | 1206 | Multicomp | MC1206N470J500CT | Farnell | 2320898 | 50V | 5% | NP0 | 47PF
CAPACITOR | 0.0000000001 | CAP, MLCC, C0G/NP0, 56PF, 50V, 0402 | 0402 | Multicomp | MC0402N560J500CT | Farnell | 1758961 | 50V | 5% | NP0 | 56PF
CAPACITOR | 0.0000000001 | CAP, MLCC, C0G/NP0, 56PF, 50V, 0603 | 0603 | Multicomp | MC0603N560J500CT | Farnell | 1759063 | 50V | 5% | NP0 | 56PF
CAPACITOR | 0.0000000001 | CAP, MLCC, C0G/NP0, 56PF, 50V, 0805 | 0805 | AVX | 08055A560JAT2A | Farnell | 2332775 | 50V | 5% | NPO | 56PF
CAPACITOR | 0.0000000001 | CAP CERAM, COG, 56PF 50V, 1206 | 1206 | Kemet | C1206C560J5GACTU | Farnell | 1164014 | 50V | 5% | NP0 | 56PF
CAPACITOR | 0.0000000001 | CAP, MLCC, C0G/NP0, 68PF, 50V, 0402 | 0402 | Multicomp | MC0402N680J500CT | Farnell | 1758964 | 50V | 5% | NP0 | 68PF
CAPACITOR | 0.0000000001 | CAP, MLCC, C0G/NP0, 68PF, 50V, 0603 | 0603 | Multicomp | MC0603N680J500CT | Farnell | 1759064 | 50V | 5% | NP0 | 68PF
CAPACITOR | 0.0000000001 | CAP, MLCC, C0G/NP0, 68PF, 50V, 0805 | 0805 | Multicomp | MC0805N680J500CT | Farnell | 1759201 | 50V | 5% | NP0 | 68PF
CAPACITOR | 0.0000000001 | CAP, MLCC, C0G/NP0, 68PF, 50V, 1206 | 1206 | AVX | 12065A680JAT2A | Farnell | 2332874 | 50V | 5% | NP0 | 68PF
CAPACITOR | 0.0000000001 | CAP, MLCC, C0G/NP0, 82PF, 50V, 0603 | 0603 | Multicomp | MC0603N820J500CT | Farnell | 1759065 | 50V | 5% | NP0 | 82PF
CAPACITOR | 0.0000000001 | CAP, MLCC, C0G/NP0, 82PF, 50V, 0805 | 0805 | Multicomp | MC0805N820J500CT | Farnell | 1759202 | 50V | 5% | NP0 | 82PF
CAPACITOR | 0.0000000001 | CAP, MLCC, C0G/NP0, 100PF, 50V, 0402 | 0402 | Multicomp | MC0402N101J500CT | Farnell | 1758969 | 50V | 5% | NP0 | 100PF
CAPACITOR | 0.0000000001 | CAP, MLCC, C0G/NP0, 100PF, 50V, 0603 | 0603 | Multicomp | MC0603N101J500CT | Farnell | 1759066 | 50V | 5% | NP0 | 100PF
CAPACITOR | 0.0000000001 | CAP, MLCC, C0G/NP0, 100PF, 50V, 0805 | 0805 | Multicomp | MC0805N101J500CT | Farnell | 1759203 | 50V | 5% | NP0 | 100PF
CAPACITOR | 0.0000000001 | CAP, MLCC, C0G/NP0, 100PF, 50V, 1206 | 1206 | Multicomp | MC1206N101J500CT | Farnell | 1759327 | 50V | 5% | NP0 | 100PF
CAPACITOR | 0.0000000001 | CAP, MLCC, C0G/NP0, 120PF, 50V, 0603 | 0603 | Multicomp | MC0603N121J500CT | Farnell | 1759067 | 50V | 5% | NP0 | 120PF
CAPACITOR | 0.0000000001 | CAP, MLCC, C0G/NP0, 120PF, 50V, 0805 | 0805 | MULTICOMP | MCCA000331 | Farnell | 1759204 | 50V | 5% | NPO | 120PF
CAPACITOR | 0.0000000001 | CAP, MLCC, C0G/NP0, 150PF, 50V, 0402 | 0402 | Multicomp | MC0402N151J500CT | Farnell | 1758976 | 50V | 5% | NP0 | 150PF
CAPACITOR | 0.0000000001 | CAP, MLCC, C0G/NP0, 150PF, 50V, 0603 | 0603 | Multicomp | MC0603N151J500CT | Farnell | 1759068 | 50V | 5% | NP0 | 150PF
CAPACITOR | 0.0000000001 | CAP, MLCC, C0G/NP0, 150PF, 50V, 0805 | 0805 | Multicomp | MC0805N151J500CT | Farnell | 1759205 | 50V | 5% | NP0 | 150PF
CAPACITOR | 0.0000000001 | CAP, MLCC, C0G/NP0, 150PF, 50V, 1206 | 1206 | Kemet | C1206C151J5GACTU | Farnell | 1800829 | 50V | 5% | NP0 | 150PF
CAPACITOR | 0.0000000002 | CAP, MLCC, C0G/NP0, 180PF, 50V, 0603 | 0603 | Multicomp | MC0603N181J500CT | Farnell | 1759069 | 50V | 5% | NP0 | 180PF
CAPACITOR | 0.0000000002 | CAP, MLCC, C0G/NP0, 180PF, 50V, 0805 | 0805 | MULTICOMP | MCCA000333 | Farnell | 1759207 | 50V | 5% | NPO | 180PF
CAPACITOR | 0.0000000002 | CAP, MLCC, C0G/NP0, 220PF, 50V, 0402 | 0402 | Multicomp | MC0402N221J500CT | Farnell | 1758982 | 50V | 5% | NP0 | 220PF
CAPACITOR | 0.0000000002 | CAP, MLCC, C0G/NP0, 220PF, 50V, 0603 | 0603 | Multicomp | MC0603N221J500CT | Farnell | 1759071 | 50V | 5% | NP0 | 220PF
CAPACITOR | 0.0000000002 | CAP, MLCC, C0G/NP0, 220PF, 50V, 0805 | 0805 | Multicomp | MC0805N221J500CT | Farnell | 1759209 | 50V | 5% | NP0 | 220PF
CAPACITOR | 0.0000000002 | CAP, MLCC, C0G/NP0, 220PF, 50V, 1206 | 1206 | Multicomp | MC1206N221J500CT | Farnell | 2320892 | 50V | 5% | NP0 | 220PF
CAPACITOR | 0.0000000003 | CAP, MLCC, C0G/NP0, 270PF, 50V, 0603 | 0603 | Multicomp | MC0603N271J500CT | Farnell | 1759074 | 50V | 5% | NP0 | 270PF
CAPACITOR | 0.0000000003 | CAP, MLCC, C0G/NP0, 270PF, 50V, 0805 | 0805 | Multicomp | MC0805N271J500CT | Farnell | 1759211 | 50V | 5% | NP0 | 270PF
CAPACITOR | 0.0000000003 | CAP, MLCC, C0G/NP0, 330PF, 50V, 0402 | 0402 | Multicomp | MC0402N331J500CT | Farnell | 2320763 | 50V | 5% | NP0 | 330PF
CAPACITOR | 0.0000000003 | CAP, MLCC, C0G/NP0, 330PF, 50V, 0603 | 0603 | Multicomp | MC0603N331J500CT | Farnell | 1759076 | 50V | 5% | C0G | 330PF
CAPACITOR | 0.0000000003 | CAP, MLCC, C0G/NP0, 330PF, 50V, 0805 | 0805 | Multicomp | MC0805N331J500CT | Farnell | 1759213 | 50V | 5% | NP0 | 330PF
CAPACITOR | 0.0000000003 | CAP, MLCC, 330PF, 50V, NP0, 1206 | 1206 | Multicomp | MC1206N331J500CT | Farnell | 2341525 | 50V | 5% | NP0 | 330PF
CAPACITOR | 0.0000000004 | CAP, MLCC, C0G/NP0, 390PF, 50V, 0603 | 0603 | Multicomp | MCCA000215 | Farnell | 1759078 | 50V | 5% | C0G | 390PF
CAPACITOR | 0.0000000004 | CAP, MLCC, C0G/NP0, 390PF, 50V, 0805 | 0805 | MULTICOMP | MCCA000341 | Farnell | 1759215 | 50V | 5% | NPO | 390PF
CAPACITOR | 0.0000000004 | CAP, MLCC, C0G/NP0, 390PF, 50V, 1206 | 1206 | AVX | 12065A391JAT2A | Farnell | 2332871 | 50V | 5% | NP0 | 390PF
CAPACITOR | 0.0000000005 | CAP, MLCC, C0G/NP0, 470PF, 50V, 0402 | 0402 | Multicomp | MC0402N471J500CT | Farnell | 2320764 | 50V | 5% | NP0 | 470PF
CAPACITOR | 0.0000000005 | CAP, MLCC, C0G/NP0, 470PF, 50V, 0603 | 0603 | Multicomp | MC0603N471J500CT | Farnell | 1759080 | 50V | 5% | NP0 | 470PF
CAPACITOR | 0.0000000005 | CAP, MLCC, C0G/NP0, 470PF, 50V, 0805 | 0805 | Multicomp | MC0805N471J500CT | Farnell | 1759217 | 50V | 5% | NP0 | 470PF
CAPACITOR | 0.0000000005 | CAP, MLCC, 470PF, 50V, NP0, 1206 | 1206 | Multicomp | MC1206N471J500CT | Farnell | 2341531 | 50V | 5% | NP0 | 470PF
CAPACITOR | 0.0000000006 | CAP, MLCC, C0G/NP0, 560PF, 50V, 0402 | 0402 | Kemet | C0402C561J5GACTU | Farnell | 1572620 | 50V | 5% | NP0 | 560PF
CAPACITOR | 0.0000000006 | CAP, MLCC, C0G/NP0, 560PF, 50V, 0603 | 0603 | Multicomp | MC0603N561J500CT | Farnell | 1759082 | 50V | 5% | NP0 | 560PF
CAPACITOR | 0.0000000006 | CAP, MLCC, C0G/NP0, 560PF, 50V, 0805 | 0805 | Multicomp | MC0805N561J500CT | Farnell | 1759221 | 50V | 5% | NP0 | 560PF
CAPACITOR | 0.0000000006 | CAP, MLCC, C0G/NP0, 560PF, 50V, 1206 | 1206 | Multicomp | MCS1206N561J1HRN-P4-RH | Farnell | 1650923 | 50V | 5% | NP0 | 560PF
CAPACITOR | 0.0000000007 | CAP, MLCC, X7R, 680PF, 50V, 0402 | 0402 | Multicomp | MCCA000134 | Farnell | 1758989 | 50V | 10% | X7R | 680PF
CAPACITOR | 0.0000000007 | CAP, MLCC, C0G/NP0, 680PF, 50V, 0603 | 0603 | Multicomp | MC0603N681J500CT | Farnell | 1759084 | 50V | 5% | NP0 | 680PF
CAPACITOR | 0.0000000007 | CAP, MLCC, C0G/NP0, 680PF, 50V, 0805 | 0805 | Multicomp | MC0805N681J500CT | Farnell | 1759223 | 50V | 5% | NP0 | 680PF
CAPACITOR | 0.0000000008 | CAP, MLCC, C0G/NP0, 820PF, 50V, 0402 | 0402 | Kemet | C0402C821J5GACTU | Farnell | 1800801 | 50V | 5% | NP0 | 820PF
CAPACITOR | 0.0000000008 | CAP, MLCC, C0G/NP0, 820PF, 50V,0603 | 0603 | MULTICOMP | MC0603N821J500CT | Farnell | 2310596 | 50V | 5% | NPO | 820PF
CAPACITOR | 0.0000000008 | CAP, MLCC, C0G/NP0, 820PF, 50V, 0805 | 0805 | Multicomp | MC0805N821J500CT | Farnell | 1759225 | 50V | 5% | NP0 | 820PF
CAPACITOR | 0.0000000008 | CAP, MLCC, C0G/NP0, 820PF, 50V, 1206 | 1206 | AVX | 12065A821JAT2A | Farnell | 2332878 | 50V | 5% | NP0 | 820PF
CAPACITOR | 0.0000000010 | CAP, MLCC, X7R, 1NF, 50V, 0402 | 0402 | Multicomp | MC0402B102K500CT | Farnell | 1758991 | 50V | 10% | X7R | 1NF
CAPACITOR | 0.0000000010 | CAP CERAM 1000PF 50V,C0G,5%,0603 | 0603 | YAGEO | CC0603JRNPO9BN102 | Farnell | 2370662 | 50V | 5% | COG | 1NF
CAPACITOR | 0.0000000010 | CAP, MLCC,C0G/NP0,1NF,50V,0805 | 0805 | AVX | 08055A102JAT2A | Farnell | 317457 | 50V | 5% | NP0 | 1NF
CAPACITOR | 0.0000000010 | CAP, MLCC,C0G/NP0,1NF,50V,1206 | 1206 | AVX | 12065A102JAT2A | Farnell | 2281069 | 50V | 5% | NP0 | 1NF
CAPACITOR | 0.0000000012 | CAP, MLCC,C0G/NP0,1.2NF,50V,0603 | 0603 | Kemet | C0603C122J5GACTU | Farnell | 1813421 | 50V | 5% | C0G | 1.2NF
CAPACITOR | 0.0000000012 | CAP, MLCC,C0G/NP0,1.2NF,50V, 0805 | 0805 | MULTICOMP | MCCA000353 | Farnell | 1759229 | 50V | 5% | NPO | 1.2NF
CAPACITOR | 0.0000000015 | CAP, MLCC, X7R, 1.5NF, 50V, 0402 | 0402 | Multicomp | MC0402B152K500CT | Farnell | 1758993 | 50V | 10% | X7R | 1.5NF
CAPACITOR | 0.0000000015 | CAP, MLCC, X7R, 1.5NF, 50V, 0603 | 0603 | Multicomp | MC0603B152K500CT | Farnell | 1759091 | 50V | 10% | X7R | 1.5NF
CAPACITOR | 0.0000000015 | CAP, MLCC,C0G/NP0,1.5NF,50V,0805 | 0805 | Multicomp | MC0805N152J500CT | Farnell | 1759230 | 50V | 5% | NP0 | 1.5NF
CAPACITOR | 0.0000000015 | CAP, MLCC, X7R, 5.6NF, 50V, 1206 | 1206 | Multicomp | MCCA000466 | Farnell | 1759347 | 50V | 10% | X7R | 1.5NF
CAPACITOR | 0.0000000018 | CAP, MLCC,C0G/NP0,1.8NF,25V,0402 | 0402 | Kemet | C0402C182J3GACTU | Farnell | 1800793 | 25V | 5% | NP0 | 1.8NF
CAPACITOR | 0.0000000018 | CAP, MLCC, X7R, 1.8NF, 50V, 0603 | 0603 | Multicomp | MCCA000228 | Farnell | 1759092 | 50V | 10% | X7R | 1.8NF
CAPACITOR | 0.0000000018 | CAP, MLCC, X7R, 1.8NF, 50V, 0805 | 0805 | MULTICOMP | MCCA000356 | Farnell | 1759233 | 50V | 10% | Z7R | 1.8NF
CAPACITOR | 0.0000000022 | CAP, MLCC, X7R, 2.2NF, 50V, 0402 | 0402 | Multicomp | MC0402B222K500CT | Farnell | 1758995 | 50V | 10% | X7R | 2.2NF
CAPACITOR | 0.0000000022 | CAP, MLCC, X7R, 2.2NF, 50V, 0603 | 0603 | Multicomp | MC0603B222K500CT | Farnell | 1759093 | 50V | 10% | X7R | 2.2NF
CAPACITOR | 0.0000000022 | CAP, MLCC, X7R, 2.2NF, 50V, 0805 | 0805 | Multicomp | MC0805B222K500CT | Farnell | 1759235 | 50V | 10% | X7R | 2.2NF
CAPACITOR | 0.0000000022 | CAP, MLCC, X7R, 2.2NF, 50V, 1206 | 1206 | Multicomp | MC1206B222K500CT | Farnell | 1759341 | 50V | 10% | X7R | 2.2NF
CAPACITOR | 0.0000000027 | CAP, MLCC, X7R, 2.7NF, 50V, 0402 | 0402 | Multicomp | MCCA000141 | Farnell | 1758996 | 50V | 10% | X7R | 2.7NF
CAPACITOR | 0.0000000027 | CAP, MLCC, X7R, 2.7NF, 50V, 0603 | 0603 | Multicomp | MCCA000230 | Farnell | 1759094 | 50V | 10% | X7R | 2.7NF
CAPACITOR | 0.0000000027 | CAP, MLCC, X7R, 2.7NF, 50V, 0805 | 0805 | MULTICOMP | MCCA000360 | Farnell | 1759237 | 50V | 10% | X7R | 2.7NF
CAPACITOR | 0.0000000033 | CAP, MLCC, X7R, 3.3NF, 50V, 0402 | 0402 | Multicomp | MC0402B332K500CT | Farnell | 1758997 | 50V | 10% | X7R | 3.3NF
CAPACITOR | 0.0000000033 | CAP, MLCC, X7R, 3.3NF, 50V, 0603 | 0603 | Multicomp | MC0603B332K500CT | Farnell | 1759095 | 50V | 10% | X7R | 3.3NF
CAPACITOR | 0.0000000033 | CAP, MLCC, X7R, 3.3NF, 50V, 0805 | 0805 | Multicomp | MC0805B332K500CT | Farnell | 1759239 | 50V | 10% | X7R | 3.3NF
CAPACITOR | 0.0000000033 | CAP, MLCC, X7R, 3.3NF, 50V, 1206 | 1206 | Multicomp | MC1206B332K500CT | Farnell | 1759343 | 50V | 10% | X7R | 3.3NF
CAPACITOR | 0.0000000047 | CAP, MLCC, X5R, 4.7UF, 6.3V, 0402 | 0402 | Murata | GRM155R60J475ME87D | Farnell | 2362092 | 6.3V | 20% | X5R | 4.7UF
CAPACITOR | 0.0000000047 | CAP, MLCC, X7R, 4.7NF, 50V, 0402 | 0402 | Multicomp | MC0402B472K500CT | Farnell | 2320772 | 50V | 10% | X7R | 4.7NF
CAPACITOR | 0.0000000047 | CAP, MLCC, X5R, 4.7UF, 6.3V, 0603 | 0603 | Multicomp | MC0603X475K6R3CT | Farnell | 2320811 | 6.3V | 10% | X5R | 4.7UF
CAPACITOR | 0.0000000047 | CAP, MLCC, X7R, 4.7NF, 50V, 0603 | 0603 | Multicomp | MC0603B472K500CT | Farnell | 1759098 | 50V | 10% | X7R | 4.7NF
CAPACITOR | 0.0000000047 | CAP, MLCC, X5R, 4.7UF, 16V, 0805 | 0805 | Multicomp | MC0805X475K160CT | Farnell | 1759428 | 16V | 10% | X5R | 4.7UF
CAPACITOR | 0.0000000047 | CAP, MLCC, X7R, 4.7NF, 50V, 0805 | 0805 | Multicomp | MC0805B472K500CT | Farnell | 1759241 | 50V | 10% | X7R | 4.7NF
CAPACITOR | 0.0000000047 | CAP, MLCC, X7R, 4.7UF, 25V, 1206 | 1206 | Multicomp | MC1206B475K250CT | Farnell | 2320886 | 25V | 10% | X7R | 4.7UF
CAPACITOR | 0.0000000047 | CAP, MLCC, X7R, 4.7NF, 50V, 1206 | 1206 | Multicomp | MC1206B472K500CT | Farnell | 1759345 | 50V | 10% | X7R | 4.7NF
CAPACITOR | 0.0000000056 | CAP, MLCC, X7R, 5.6NF, 50V, 0603 | 0603 | Multicomp | MCCA000234 | Farnell | 1759099 | 50V | 10% | X7R | 5.6NF
CAPACITOR | 0.0000000056 | CAP, MLCC, X7R, 5.6NF, 50V, 0805 | 0805 | MULTICOMP | MCCA000365 | Farnell | 1759242 | 50V | 10% | X7R | 5.6NF
CAPACITOR | 0.0000000068 | CAP, MLCC, X7R, 6.8NF, 50V, 0603 | 0603 | Multicomp | MC0603B682K500CT | Farnell | 1759100 | 50V | 10% | X7R | 6.8NF
CAPACITOR | 0.0000000068 | CAP, MLCC, X7R, 6.8NF, 50V, 0805 | 0805 | Multicomp | MC0805B682K500CT | Farnell | 1759244 | 50V | 10% | X7R | 6.8NF
CAPACITOR | 0.0000000082 | CAP, MLCC, X7R, 8.2NF, 50V, 0603 | 0603 | Multicomp | MCCA000236 | Farnell | 1759101 | 50V | 10% | X7R | 8.2NF
CAPACITOR | 0.0000000082 | CAP, MLCC, X7R, 8.2NF, 50V, 0805 | 0805 | AVX | 08055C822KAT2A | Farnell | 2332807 | 50V | 10% | X7R | 8.2NF
CAPACITOR | 0.0000000082 | CAP, MLCC, X7R, 8.2NF, 50V, 1206 | 1206 | MULTICOMP | MCCA000468 | Farnell | 1759349 | 50V | 10% | X7R | 8.2NF
CAPACITOR | 0.0000000100 | CAP, MLCC, X7R, 10NF, 25V, 0402 | 0402 | Multicomp | MC0402B103K250CT | Farnell | 1758924 | 25V | 10% | X7R | 10NF
CAPACITOR | 0.0000000100 | CAP, MLCC, X7R, 10NF, 50V, 0603 | 0603 | Multicomp | MC0603B103K500CT | Farnell | 1759102 | 50V | 10% | X7R | 10NF
CAPACITOR | 0.0000000100 | CAP, MLCC, X7R, 10NF, 50V, 0805 | 0805 | Multicomp | MC0805B103K500CT | Farnell | 1759246 | 50V | 10% | X7R | 10NF
CAPACITOR | 0.0000000100 | CAP, MLCC, X7R, 10NF, 50V, 1206 | 1206 | Multicomp | MC1206B103K500CT | Farnell | 1759350 | 50V | 10% | X7R | 10NF
CAPACITOR | 0.0000000120 | CAP, MLCC, X7R, 12NF, 50V, 0603 | 0603 | Multicomp | MCCA000239 | Farnell | 1759105 | 50V | 10% | X7R | 12NF
CAPACITOR | 0.0000000120 | CAP, MLCC, X7R, 12NF, 50V, 0805 | 0805 | MULTICOMP | MCCA000370 | Farnell | 1759248 | 50V | 10% | X7R | 12NF
CAPACITOR | 0.0000000150 | CAP, MLCC, C0G/NP0,15PF,50V,0402 | 0402 | Multicomp | MC0402N150J500CT | Farnell | 1758945 | 50V | 5% | NP0 | 15PF
CAPACITOR | 0.0000000150 | CAP, MLCC, X7R, 15NF, 16V, 0402 | 0402 | Multicomp | MCCA000042 | Farnell | 1758887 | 16V | 10% | X7R | 15NF
CAPACITOR | 0.0000000150 | CAP, MLCC, X7R, 15NF, 50V, 0603 | 0603 | Multicomp | MC0603B153K500CT | Farnell | 1759106 | 50V | 10% | X7R | 15NF
CAPACITOR | 0.0000000150 | CAP, MLCC, X7R, 15NF, 50V, 0805 | 0805 | Multicomp | MC0805B153K500CT | Farnell | 1759249 | 50V | 10% | X7R | 15NF
CAPACITOR | 0.0000000180 | CAP, MLCC, X7R, 18NF, 50V, 0603 | 0603 | Multicomp | MCCA000242 | Farnell | 1759108 | 50V | 10% | X7R | 18NF
CAPACITOR | 0.0000000220 | CAP, MLCC, X7R, 22NF, 25V, 0402 | 0402 | TDK | C1005X7R1E223K050BB | Farnell | 1907262 | 25V | 10% | X7R | 22NF
CAPACITOR | 0.0000000220 | CAP, MLCC, X7R, 22NF, 50V, 0603 | 0603 | Multicomp | MC0603B223K500CT | Farnell | 1759109 | 50V | 10% | X7R | 22NF
CAPACITOR | 0.0000000220 | CAP, MLCC, X7R, 22NF, 50V, 0805 | 0805 | Multicomp | MC0805B223K500CT | Farnell | 1759252 | 50V | 10% | X7R | 22NF
CAPACITOR | 0.0000000220 | CAP, MLCC, X7R, 22NF, 50V, 1206 | 1206 | Multicomp | MC1206B223K500CT | Farnell | 1759354 | 50V | 10% | X7R | 22NF
CAPACITOR | 0.0000000270 | CAP, MLCC, X7R, 27NF, 25V, 0402 | 0402 | Kemet | C0402C273K3RACTU | Farnell | 1865443 | 25V | 10% | X7R | 27NF
CAPACITOR | 0.0000000330 | CAP, MLCC, Y5V, 33NF, 16V, 0402 | 0402 | Multicomp | MCCA000047 | Farnell | 1758892 | 16V | +80,-20% | Y5V | 33NF
CAPACITOR | 0.0000000330 | CAP, MLCC, X7R, 33NF, 50V, 0603 | 0603 | Multicomp | MC0603B333K500CT | Farnell | 1759112 | 50V | 10% | X7R | 33NF
CAPACITOR | 0.0000000330 | CAP, MLCC, X7R, 33NF, 50V, 0805 | 0805 | Multicomp | MC0805B333K500CT | Farnell | 1759257 | 50V | 10% | X7R | 33NF
CAPACITOR | 0.0000000330 | CAP, MLCC, X7R, 33NF, 50V, 1206 | 1206 | Multicomp | MC1206B333K500CT | Farnell | 1759356 | 50V | 10% | X7R | 33NF
CAPACITOR | 0.0000000470 | CAP, MLCC, X7R, 47NF, 16V, 0402 | 0402 | TDK | CGA2B2X7R1C473K050BA | Farnell | 2210792 | 16V | 10% | X7R | 47NF
CAPACITOR | 0.0000000470 | CAP, MLCC, X7R, 47NF, 50V, 0603 | 0603 | Multicomp | MC0603B473K500CT | Farnell | 1759116 | 50V | 10% | X7R | 47NF
CAPACITOR | 0.0000000470 | CAP, MLCC, X7R, 47NF, 50V, 0805 | 0805 | Multicomp | MC0805B473K500CT | Farnell | 1759260 | 50V | 10% | X7R | 47NF
CAPACITOR | 0.0000000470 | CAP, MLCC, X7R, 47NF, 50V, 1206 | 1206 | Multicomp | MC1206B473K500CT | Farnell | 1759359 | 50V | 10% | X7R | 47NF
CAPACITOR | 0.0000000560 | CAP, MLCC, X7R, 56NF, 16V, 0603 | 0603 | Multicomp | MCCA000156 | Farnell | 1759013 | 16V | 10% | X7R | 56NF
CAPACITOR | 0.0000000560 | CAP, MLCC, X7R, 56NF, 50V, 0805 | 0805 | MULTICOMP | MCCA000382 | Farnell | 1759261 | 50V | 10% | X7R | 56NF
CAPACITOR | 0.0000000680 | CAP, MLCC, Y5V, 68NF, 16V, 0402 | 0402 | YAGEO (PHYCOMP) | CC0402ZRY5V7BB683 | Farnell | 3019470 | 16V | +80%/-20% | Y5V | 68NF
CAPACITOR | 0.0000000680 | CAP, MLCC, X7R, 68NF, 50V, 0603 | 0603 | Multicomp | MC0603B683K500CT | Farnell | 1759119 | 50V | 10% | X7R | 68NF
CAPACITOR | 0.0000000680 | CAP, MLCC, X7R, 68NF, 50V, 0805 | 0805 | Multicomp | MC0805B683K500CT | Farnell | 1759262 | 50V | 10% | X7R | 68NF
CAPACITOR | 0.0000000680 | CAP, MLCC, X7R, 68NF, 50V, 1206 | 1206 | YAGEO (PHYCOMP) | CC1206KRX7R9BB683 | Farnell | 718634 | 50V | 10% | X7R | 68NF
CAPACITOR | 0.0000000820 | CAP, MLCC, X7R, 82NF, 50V, 0603 | 0603 | Multicomp | MCCA000254 | Farnell | 1759121 | 50V | 10% | X7R | 82NF
CAPACITOR | 0.0000000820 | CAP, MLCC, X7R, 82NF, 50V, 0805 | 0805 | MULTICOMP | MCCA000385 | Farnell | 1759264 | 50V | 10% | X7R | 82NF
CAPACITOR | 0.0000001000 | CAP, MLCC, X5R, 100NF, 25V, 0402 | 0402 | Multicomp | MC0402X104K250CT | Farnell | 2320760 | 25V | 10% | X5R | 100NF
CAPACITOR | 0.0000001000 | CAP, MLCC, X7R, 100NF, 16V, 0402 | 0402 | Multicomp | MC0402B104K160CT | Farnell | 1758896 | 16V | 10% | X7R | 100NF
CAPACITOR | 0.0000001000 | CAP, MLCC, X7R, 100NF, 50V, 0603 | 0603 | Multicomp | MC0603B104K500CT | Farnell | 1759122 | 50V | 10% | X7R | 100NF
CAPACITOR | 0.0000001000 | CAP, MLCC, X7R, 100NF, 25V, 0603 | 0603 | Multicomp | MC0603B104K250CT | Farnell | 1759037 | 25V | 10% | X7R | 100NF
CAPACITOR | 0.0000001000 | CAP, MLCC, X7R, 100NF, 100V, 0805 | 0805 | Multicomp | MC0805B104K101CT | Farnell | 2320821 | 100V | 10% | X7R | 100NF
CAPACITOR | 0.0000001000 | CAP, MLCC, X7R, 100NF,50V,0805 | 0805 | Multicomp | MC0805B104K500CT | Farnell | 1759265 | 50V | 10% | X7R | 100NF
CAPACITOR | 0.0000001000 | CAP, MLCC, X7R, 100NF, 100V, 1206 | 1206 | Multicomp | MC1206B104K101CT | Farnell | 1759366 | 100V | 10% | X7R | 100NF
CAPACITOR | 0.0000001000 | CAP, MLCC, X7R, 100NF, 50V, 1206 | 1206 | Multicomp | MC1206B104K500CT | Farnell | 1759361 | 50V | 10% | X7R | 100NF
CAPACITOR | 0.0000001500 | CAP, MLCC, X7R, 150NF, 10V, 0603 | 0603 | Multicomp | MC0603B154K100CT | Farnell | 2320815 | 10V | 10% | X7R | 150NF
CAPACITOR | 0.0000001500 | CAP, MLCC, X7R, 150NF, 50V, 0805 | 0805 | KEMET | C0805C154K5RACAUTO | Farnell | 2070452 | 50V | 10% | X7R | 150NF
CAPACITOR | 0.0000001800 | CAP, MLCC, X7R, 180NF, 25V, 0603 | 0603 | Kemet | C0603C184K3RACTU | Farnell | 1865528 | 25V | 10% | X7R | 180NF
CAPACITOR | 0.0000001800 | CAP, MLCC, X7R, 180NF, 25V, 1206 | 1206 | MULTICOMP | MCCA000437 | Farnell | 1759315 | 25V | 10% | X7R | 180NF
CAPACITOR | 0.0000002200 | CAP, MLCC, X5R, 220NF, 16V, 0402 | 0402 | Multicomp | MCCA000513 | Farnell | 1759389 | 16V | 10% | X5R | 220NF
CAPACITOR | 0.0000002200 | CAP, MLCC, X7R, 220NF, 25V, 0603 | 0603 | Multicomp | MC0603B224K250CT | Farnell | 2320795 | 25V | 10% | X7R | 220NF
CAPACITOR | 0.0000002200 | CAP, MLCC, X7R, 220NF, 50V, 0805 | 0805 | Multicomp | MC0805B224K500CT | Farnell | 2320842 | 50V | 10% | X7R | 220NF
CAPACITOR | 0.0000002200 | CAP, MLCC, X7R, 220NF, 50V, 1206 | 1206 | Multicomp | MC1206B224K500CT | Farnell | 1759362 | 50V | 10% | X7R | 220NF
CAPACITOR | 0.0000003300 | CAP CERAM 0.33UF,16V,X5R,10%,0402 | 0402 | TDK | C1005X5R1C334K050BB | Farnell | 1844121 | 16V | 10% | X5R | 330NF
CAPACITOR | 0.0000003300 | CAP, MLCC, X5R, 330NF, 16V, 0603 | 0603 | Multicomp | MC0603X334K160CT | Farnell | 1759404 | 16V | 10% | X5R | 330NF
CAPACITOR | 0.0000003300 | CAP, MLCC, X7R, 330NF, 50V, 0805 | 0805 | Multicomp | MC0805B334K500CT | Farnell | 2320844 | 50V | 10% | X7R | 330NF
CAPACITOR | 0.0000003300 | CAP, MLCC, X7R, 330NF, 25V, 1206 | 1206 | Multicomp | MC1206B334K250CT | Farnell | 1759318 | 25V | 10% | X7R | 330NF
CAPACITOR | 0.0000003900 | CAP, MLCC, X7R, 390NF, 16V, 0603 | 0603 | Kemet | C0603C394K4RACTU | Farnell | 1865527 | 16V | 10% | X7R | 390NF
CAPACITOR | 0.0000004700 | CAP, MLCC, X5R, 470NF, 10V, 0402 | 0402 | Murata | GRM155R61A474KE15D | Farnell | 1828863 | 10V | 10% | X5R | 470NF
CAPACITOR | 0.0000004700 | CAP, MLCC, X5R, 470NF, 16V, 0603 | 0603 | Multicomp | MC0603X474K160CT | Farnell | 1759405 | 16V | 10% | X5R | 470NF
CAPACITOR | 0.0000004700 | CAP, MLCC, X7R, 470NF, 50V, 0805 | 0805 | Multicomp | MC0805B474K500CT | Farnell | 2320847 | 50V | 10% | X7R | 470NF
CAPACITOR | 0.0000004700 | CAP, MLCC, X7R, 470NF, 50V, 1206 | 1206 | Multicomp | MC1206B474K500CT | Farnell | 2320907 | 50V | 10% | X7R | 470NF
CAPACITOR | 0.0000006800 | CAP, MLCC, X5R, 680NF, 10V, 0603 | 0603 | Multicomp | MCCA000520 | Farnell | 1759397 | 10V | 10% | X5R | 680NF
CAPACITOR | 0.0000006800 | CAP, MLCC, X7R, 680NF, 50V, 0805 | 0805 | Kemet | C0805C684K5RACTU | Farnell | 1414702 | 50V | 10% | X7R | 680NF
CAPACITOR | 0.0000010000 | CAP, MLCC, X5R, 1UF, 10V, 0402 | 0402 | Multicomp | MC0402X105K100CT | Farnell | 2320776 | 10V | 10% | X5R | 1UF
CAPACITOR | 0.0000010000 | CAP, MLCC, X5R, 1UF, 6.3V, 0402 | 0402 | Multicomp | MC0402X105K6R3CT | Farnell | 1759375 | 6.3V | 10% | X5R | 1UF
CAPACITOR | 0.0000010000 | CAP, MLCC, X5R, 1UF, 25V, 0603 | 0603 | Multicomp | MC0603X105K250CT | Farnell | 1759409 | 25V | 10% | X5R | 1UF
CAPACITOR | 0.0000010000 | CAP, MLCC, X5R, 1UF, 16V, 0603 | 0603 | Multicomp | MC0603X105K160CT | Farnell | 1759407 | 16V | 10% | X5R | 1UF
CAPACITOR | 0.0000010000 | CAP, MLCC, X7R, 1UF, 25V, 0805 | 0805 | Multicomp | MC0805B105K250CT | Farnell | 2320827 | 25V | 10% | X7R | 1UF
CAPACITOR | 0.0000010000 | CAP, MLCC, X7R, 1UF, 50V, 1206 | 1206 | Multicomp | MC1206B105K500CT | Farnell | 1759454 | 50V | 10% | X7R | 1UF
CAPACITOR | 0.0000010000 | CAP, MLCC, X7R, 1UF, 25V, 1206 | 1206 | Multicomp | MC1206B105K250CT | Farnell | 1759446 | 25V | 10% | X7R | 1UF
CAPACITOR | 0.0000022000 | CAP, MLCC, X5R, 2.2UF, 6.3V, 0402 | 0402 | Multicomp | MC0402X225M6R3CT | Farnell | 1759376 | 6.3V | 10% | X5R | 2.2UF
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

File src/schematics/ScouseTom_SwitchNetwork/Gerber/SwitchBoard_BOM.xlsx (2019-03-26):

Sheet: Sheet1
Part | Value | Device | Package | Description | MF | MPN | OC_FARNELL | OC_NEWARK | PACKAGE | PROD_ID | SUPPLIER
C1 | 10uF | C-EUC0805 | C0805 | CAPACITOR, European symbol
C2 | 10uF | C-EUC0805 | C0805 | CAPACITOR, European symbol
C3 | 10uF | C-EUC0805 | C0805 | CAPACITOR, European symbol
C4 | 0.1uF | C-EUC0805 | C0805 | CAPACITOR, European symbol
C5 | 0.1uF | C-EUC0805 | C0805 | CAPACITOR, European symbol
C6 | 0.1uF | C-EUC0805 | C0805 | CAPACITOR, European symbol
C7 | 0.1uF | C-EUC0805 | C0805 | CAPACITOR, European symbol
C8 | 0.1uF | C-EUC0805 | C0805 | CAPACITOR, European symbol
C9 | 2.2uF | C-EUC0805 | C0805 | CAPACITOR, European symbol
C10 | 100uF | CPOL-EUCT6032 | CT6032 | POLARIZED CAPACITOR, European symbol
C11 | 10uF | C-EUC0805 | C0805 | CAPACITOR, European symbol
C12 | 0.1uF | C-EUC0805 | C0805 | CAPACITOR, European symbol
C13 | 0.1uF | C-EUC0805 | C0805 | CAPACITOR, European symbol
C14 | 0.01uF | C-EUC0805 | C0805 | CAPACITOR, European symbol
C15 | 100uF | CPOL-EUCT6032 | CT6032 | POLARIZED CAPACITOR, European symbol
C16 | 0.1uF | C-EUC0805 | C0805 | CAPACITOR, European symbol
C17 | 0.1uF | C-EUC0805 | C0805 | CAPACITOR, European symbol
C18 | .1uF | C-EUC0805 | C0805 | CAPACITOR, European symbol
C19 | 1uF | C-EUC0805 | C0805 | CAPACITOR, European symbol
C20 | .1uF | C-EUC0805 | C0805 | CAPACITOR, European symbol
C21 | 1uF | C-EUC0805 | C0805 | CAPACITOR, European symbol
C22 | 0.1uF | C-EUC0805 | C0805 | CAPACITOR, European symbol
C23 | 0.1uF | C-EUC0805 | C0805 | CAPACITOR, European symbol
C24 | .1uF | C-EUC0805 | C0805 | CAPACITOR, European symbol
C25 | 1uF | C-EUC0805 | C0805 | CAPACITOR, European symbol
C26 | .1uF | C-EUC0805 | C0805 | CAPACITOR, European symbol
C27 | 1uF | C-EUC0805 | C0805 | CAPACITOR, European symbol
JP1 | IN | M02PTH | 1X02 | Header 2
JP2 | LiPoIN | M02PTH | 1X02 | Header 2
JP3 | LiPo | M02-JST-2MM-SMT | JST-2-SMD | Header 2
JP4 | PWR | PINHD-1X2 | 1X02 | PIN HEADER
JP5 | Shld | PINHD-1X2 | 1X02 | PIN HEADER
JP6 | Shld | PINHD-1X2 | 1X02 | PIN HEADER
JP8 | CS_IN+ | PINHD-1X1 | 1X01 | PIN HEADER
JP9 | CS_IN- | PINHD-1X1 | 1X01 | PIN HEADER
L1 | 6.8uH | WE-PD-7447779006_7332/7345_PLASTIC_BASE | WE-PD_7332/7345_PLASTIC_BASE | SMD-Shielded Power Inductors WE-PD |  | 7447779006 | 1635987 | 08P2857 | 7345 |  | Wuerth Elektronik
LED1 | YELLOW | LEDSML0805 | SML0805 | LED
LED2 | GREEN | LEDSML0805 | SML0805 | LED
LED3 | GREEN | LEDSML0805 | SML0805 | LED
LED4 | RED | LEDSML0805 | SML0805 | LED
R1 | 470 | R-EU_M0805 | M0805 | RESISTOR, European symbol
R2 | 1k | R-EU_M0805 | M0805 | RESISTOR, European symbol
R3 | 2k | R-EU_M0805 | M0805 | RESISTOR, European symbol
R4 | 2M | R-EU_M0805 | M0805 | RESISTOR, European symbol
R5 | 360k | R-EU_M0805 | M0805 | RESISTOR, European symbol
R6 | 10k | R-EU_M0805 | M0805 | RESISTOR, European symbol
R7 | 10k | R-EU_M0805 | M0805 | RESISTOR, European symbol
R8 | 1.8M | R-EU_M0805 | M0805 | RESISTOR, European symbol
R9 | 82k | R-EU_M0805 | M0805 | RESISTOR, European symbol
R10 | 200k | R-EU_M0805 | M0805 | RESISTOR, European symbol
R11 | 1k | R-EU_M0805 | M0805 | RESISTOR, European symbol
R12 | 10k | R-EU_M0805 | M0805 | RESISTOR, European symbol
R13 | 10k | R-EU_M0805 | M0805 | RESISTOR, European symbol
R14 | 4.7k | R-EU_M0805 | M0805 | RESISTOR, European symbol
R15 | 47k | R-EU_M0805 | M0805 | RESISTOR, European symbol
R16 | 1k | R-EU_M0805 | M0805 | RESISTOR, European symbol
R17 | 10k | R-EU_M0805 | M0805 | RESISTOR, European symbol
R18 | 10k | R-EU_M0805 | M0805 | RESISTOR, European symbol
R19 | 10k | R-EU_M0805 | M0805 | RESISTOR, European symbol
R20 | 10k | R-EU_M0805 | M0805 | RESISTOR, European symbol
R21 | 10k | R-EU_M0805 | M0805 | RESISTOR, European symbol
R22 | 10k | R-EU_M0805 | M0805 | RESISTOR, European symbol
R23 | 10M | R-EU_M0805 | M0805 | RESISTOR, European symbol
R24 | 10M | R-EU_M0805 | M0805 | RESISTOR, European symbol
T1 | PNP | BC807-40-PNP-SOT23-BEC | SOT23-BEC | PNP Transistror
U$1 | PINHD-3X7GAP | PINHD-3X7GAP | 3X07
U1 | MCP73831 | MCP73831 | SOT23-5 | Miniature single cell, fully integrated Li-Ion, Li-polymer charge management controller |  |  |  |  |  | IC-09995
U2 | ADG714BRUZ | ADG714BRUZ | SOP65P640X120-24N | CMOS, Low Voltage Serially Controlled, Octal SPST Switches |  | ADG714BRUZ | 9604367 | 59K1531 | TSSOP-24 |  | Analog Devices
U3 | ADG714BRUZ | ADG714BRUZ | SOP65P640X120-24N | CMOS, Low Voltage Serially Controlled, Octal SPST Switches |  | ADG714BRUZ | 9604367 | 59K1531 | TSSOP-24 |  | Analog Devices
U4 | TPS61090RSAR | VREG_TPS6103XSPARKFUNVERSION | QFN16-4X4 | TPS6103x 4A Boost - 1.8-5.5V Input, Adjustable Output to 5.5V
U5 | ADG714BRUZ | ADG714BRUZ | SOP65P640X120-24N | CMOS, Low Voltage Serially Controlled, Octal SPST Switches |  | ADG714BRUZ | 9604367 | 59K1531 | TSSOP-24 |  | Analog Devices
U6 | ADG714BRUZ | ADG714BRUZ | SOP65P640X120-24N | CMOS, Low Voltage Serially Controlled, Octal SPST Switches |  | ADG714BRUZ | 9604367 | 59K1531 | TSSOP-24 |  | Analog Devices
U7 | ADG714BRUZ | ADG714BRUZ | SOP65P640X120-24N | CMOS, Low Voltage Serially Controlled, Octal SPST Switches |  | ADG714BRUZ | 9604367 | 59K1531 | TSSOP-24 |  | Analog Devices
U8 | LT1763CDE-5 | LT1763CDE-5 | DFN12 | 500mA, Low Noise, LDO Micropower Regulators |  | LT1763CDE-5 | 1556468 | 57M6035
U9 | ADG714BRUZ | ADG714BRUZ | SOP65P640X120-24N | CMOS, Low Voltage Serially Controlled, Octal SPST Switches |  | ADG714BRUZ | 9604367 | 59K1531 | TSSOP-24 |  | Analog Devices
U10 | ADG714BRUZ | ADG714BRUZ | SOP65P640X120-24N | CMOS, Low Voltage Serially Controlled, Octal SPST Switches |  | ADG714BRUZ | 9604367 | 59K1531 | TSSOP-24 |  | Analog Devices
U11 | ADG714BRUZ | ADG714BRUZ | SOP65P640X120-24N | CMOS, Low Voltage Serially Controlled, Octal SPST Switches |  | ADG714BRUZ | 9604367 | 59K1531 | TSSOP-24 |  | Analog Devices
U12 | ADUM1410ARWZ | ADUM1410ARWZ | SOIC127P1032X265-16N | ISOLATOR, DGTL, 4CHAN |  | ADUM1410ARWZ | 2067770 | 73T8174 | 16-Lead SOIC_W |  | Analog Devices
U13 | ADG714BRUZ | ADG714BRUZ | SOP65P640X120-24N | CMOS, Low Voltage Serially Controlled, Octal SPST Switches |  | ADG714BRUZ | 9604367 | 59K1531 | TSSOP-24 |  | Analog Devices
U14 | ADG714BRUZ | ADG714BRUZ | SOP65P640X120-24N | CMOS, Low Voltage Serially Controlled, Octal SPST Switches |  | ADG714BRUZ | 9604367 | 59K1531 | TSSOP-24 |  | Analog Devices
U15 | ADUM1412ARWZ | ADUM1412ARWZ | SOIC127P1032X265-16N | IC, DIG ISOLATOR |  | ADUM1412ARWZ | 2377152 |  | 16-Lead SOIC_W |  | Analog Devices
X1 |  | 47346-0001 | MOLEX_47346-0001 | CONN RCPT 5POS MICRO USB R/A SMD |  | 47346-0001 | 1568026 | 47M0505 | 5 POS MICRO USB R/A |  | MOLEX
X2 | CTR_ARD | F09HP | F09HP | SUB-D |  |  | unknown | unknown
X3 | CTR_OUT | M09HP | M09HP | SUB-D |  |  | unknown | unknown
X4 | DSUB _T | F37HP | F37HP | SUB-D |  |  | unknown | unknown
X5 | DSUB_B | M37HP | M37HP | SUB-D |  |  | unknown | unknown
X6 | CTR_IN | F09HP | F09HP | SUB-D |  |  | unknown | unknown
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

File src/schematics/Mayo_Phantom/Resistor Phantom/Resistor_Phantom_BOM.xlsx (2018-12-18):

Part | Value | Device | Package | Description | MPN | OC_FARNELL | PCBTRAINFREE
K1 | AQY221R2S | AQY221R2S | SOP04 | PHOTOMOS Relay RF (Radio Frequency) NAiS | AQY221R2S | 1653770
K2 | AQY221R2S | AQY221R2S | SOP04 | PHOTOMOS Relay RF (Radio Frequency) NAiS | AQY221R2S | 1653770
K3 | AQY221R2S | AQY221R2S | SOP04 | PHOTOMOS Relay RF (Radio Frequency) NAiS | AQY221R2S | 1653770
R1 | 1k | R-EU_R0402 | R0402 | RESISTOR, European symbol | MC00625W040211K | 1358043 | PCBTRAINFREESTOCK
R2 | 1k | R-EU_R0402 | R0402 | RESISTOR, European symbol | MC00625W040211K | 1358043 | PCBTRAINFREESTOCK
R3 | 1k | R-EU_R0402 | R0402 | RESISTOR, European symbol | MC00625W040211K | 1358043 | PCBTRAINFREESTOCK
R4 | 1k | R-EU_R0402 | R0402 | RESISTOR, European symbol | MC00625W040211K | 1358043 | PCBTRAINFREESTOCK
R5 | 1k | R-EU_R0402 | R0402 | RESISTOR, European symbol | MC00625W040211K | 1358043 | PCBTRAINFREESTOCK
R6 | 1k | R-EU_R0402 | R0402 | RESISTOR, European symbol | MC00625W040211K | 1358043 | PCBTRAINFREESTOCK
R7 | 1k | R-EU_R0402 | R0402 | RESISTOR, European symbol | MC00625W040211K | 1358043 | PCBTRAINFREESTOCK
R8 | 1k | R-EU_R0402 | R0402 | RESISTOR, European symbol | MC00625W040211K | 1358043 | PCBTRAINFREESTOCK
R9 | 1k | R-EU_R0402 | R0402 | RESISTOR, European symbol | MC00625W040211K | 1358043 | PCBTRAINFREESTOCK
R10 | 1k | R-EU_R0402 | R0402 | RESISTOR, European symbol | MC00625W040211K | 1358043 | PCBTRAINFREESTOCK
R11 | 1k | R-EU_R0402 | R0402 | RESISTOR, European symbol | MC00625W040211K | 1358043 | PCBTRAINFREESTOCK
R12 | 1k | R-EU_R0402 | R0402 | RESISTOR, European symbol | MC00625W040211K | 1358043 | PCBTRAINFREESTOCK
R13 | 1k | R-EU_R0402 | R0402 | RESISTOR, European symbol | MC00625W040211K | 1358043 | PCBTRAINFREESTOCK
R14 | 1k | R-EU_R0402 | R0402 | RESISTOR, European symbol | MC00625W040211K | 1358043 | PCBTRAINFREESTOCK
R15 | 1k | R-EU_R0402 | R0402 | RESISTOR, European symbol | MC00625W040211K | 1358043 | PCBTRAINFREESTOCK
R16 | 1k | R-EU_R0402 | R0402 | RESISTOR, European symbol | MC00625W040211K | 1358043 | PCBTRAINFREESTOCK
R17 | 1k | R-EU_R0402 | R0402 | RESISTOR, European symbol | MC00625W040211K | 1358043 | PCBTRAINFREESTOCK
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

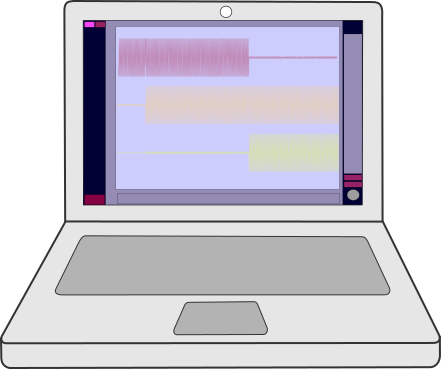
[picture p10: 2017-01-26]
doc/figures/Components/Laptop.png

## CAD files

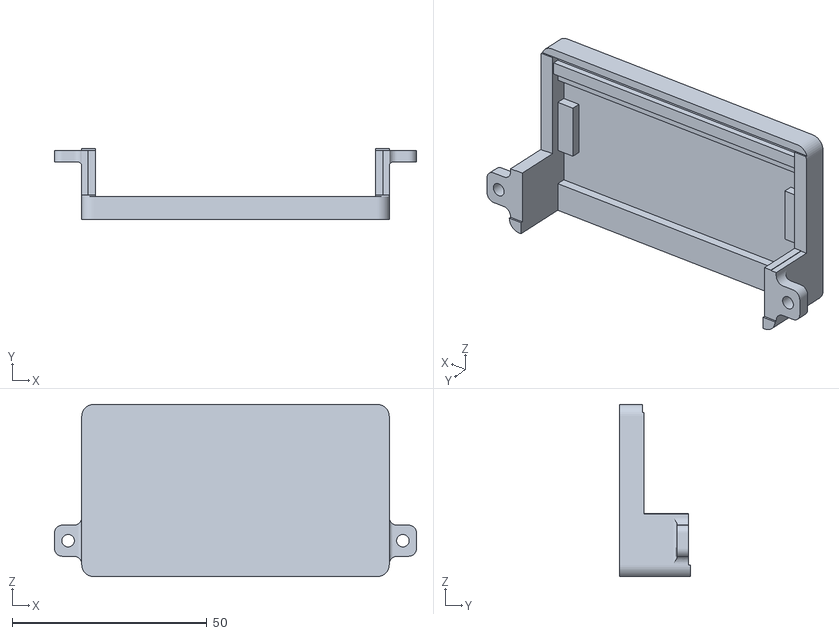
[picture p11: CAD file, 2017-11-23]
doc/case/Dsub2CrocPrintingMain.STL
93.0 x 18.3 x 44.2

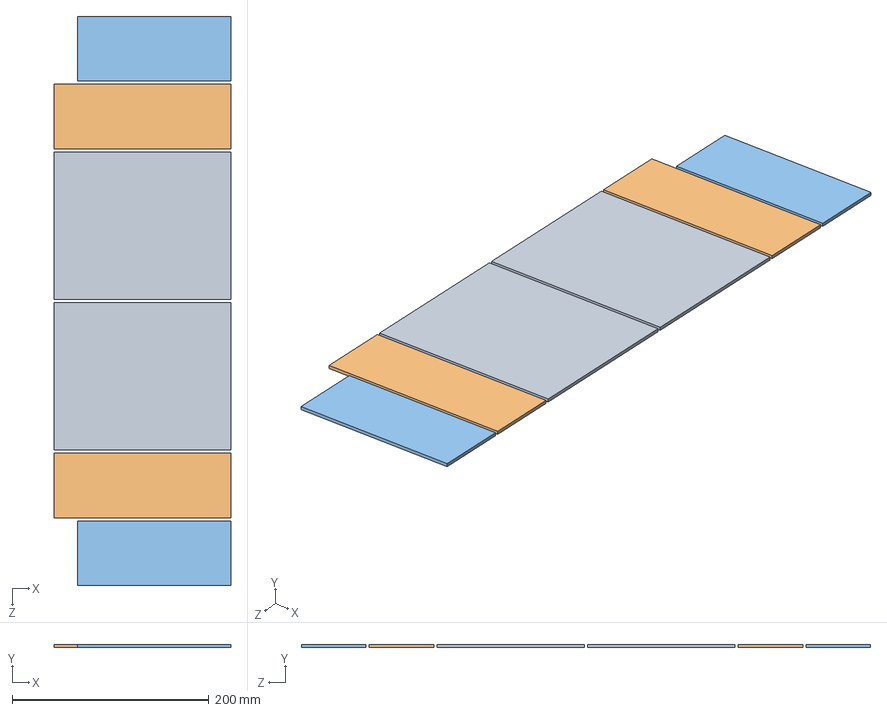
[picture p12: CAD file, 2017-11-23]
doc/ActiChamp_Simple_Box/Actichamp_simple_box_laser_cut.SLDASM
180.0 x 3.00 x 579.0 mm
Actichamp_box_base x 2
Actichamp_box_Side x 2
Actichamp_box_back x 2

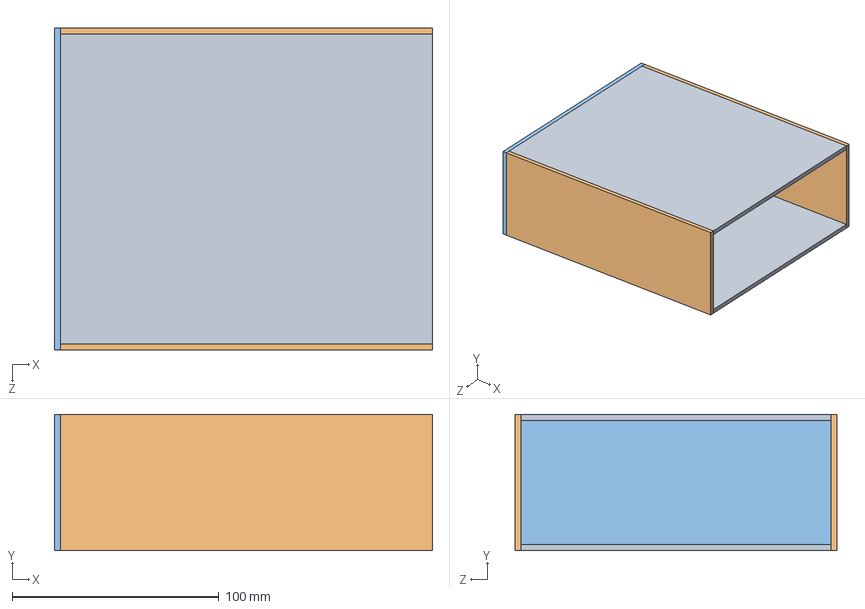
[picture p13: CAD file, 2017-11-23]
doc/ActiChamp_Simple_Box/Actichamp_simple_box.SLDASM
183.0 x 66.0 x 156.0 mm
Actichamp_box_base x 2
Actichamp_box_Side x 2
Actichamp_box_back

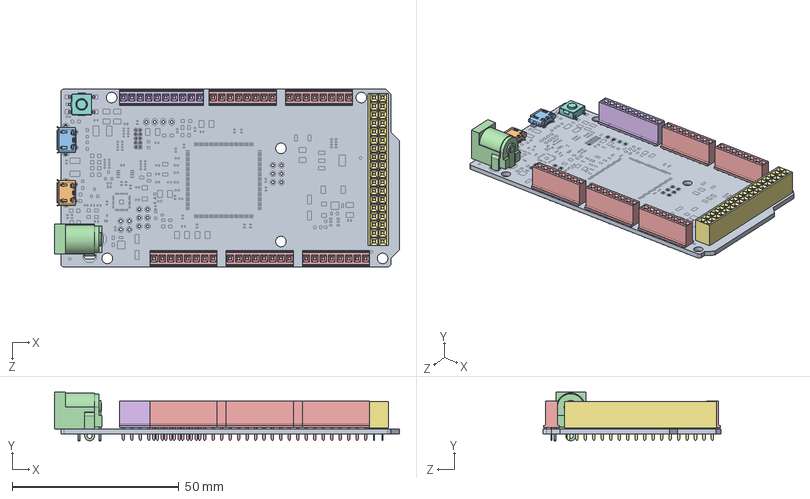
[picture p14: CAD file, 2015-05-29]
doc/case/Arduino Due/ARDUINO DUE.SLDASM
103.5 x 14.6 x 53.3 mm
PCB - Arduino
MicroUSB B - Hirose - ZX62D-B-5P8
MicroUSB AB - Hirose - ZX62D-AB-5P8
Power Jack - Kycon - KLDHCX-0202-A
Berg Header Receptacle 2.54 x 8 - FCI - 66951-008LF x 5
Berg Header Receptacle 2.54 x 10 - FCI - 66951-010LF
Berg Header Receptacle 2.54 x 36 - FCI - 66953-018LF
Switch - ESwitch - TLE3303

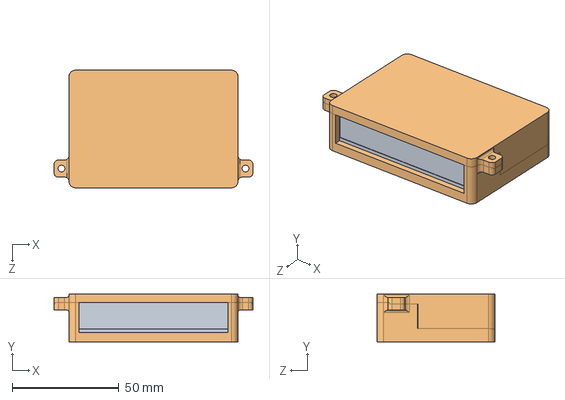
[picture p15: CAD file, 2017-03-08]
doc/case/Dsub2CrocAssembly.SLDASM
93.0 x 22.3 x 55.0 mm
Dsub2Croc
Dsub2CrocCase

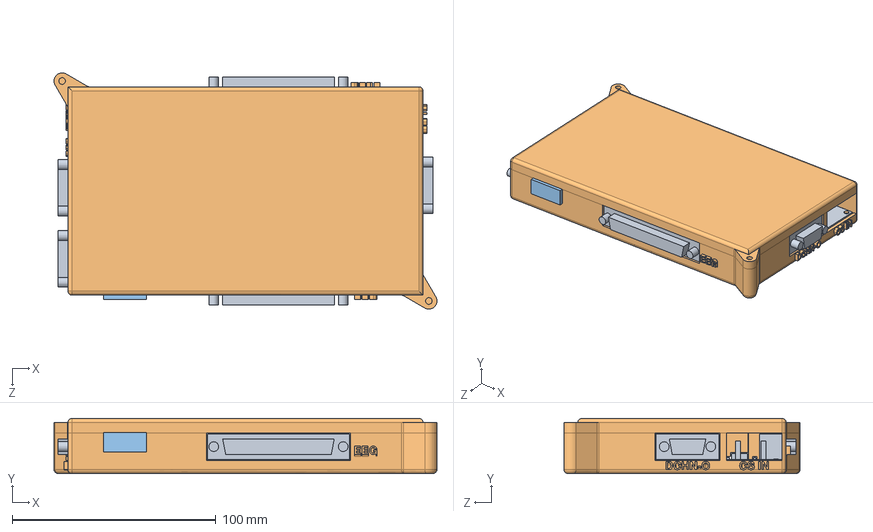
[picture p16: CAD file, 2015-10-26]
doc/case/ScouseTom_SwitchBoard_Case.SLDASM
187.9 x 27.0 x 115.9 mm
ScouseTom_SwitchBoard
SwitchBoardCase
Switch

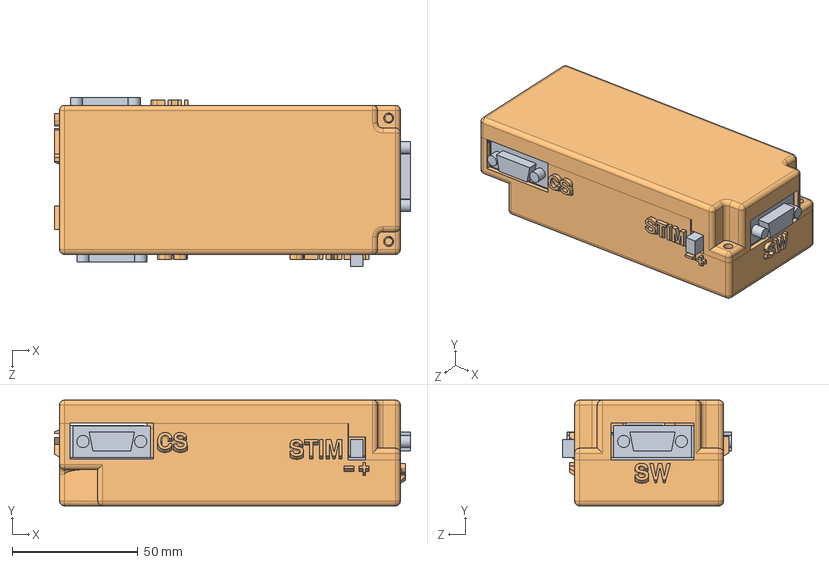
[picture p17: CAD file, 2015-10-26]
doc/case/ScouseTom_Case.SLDASM
141.3 x 42.0 x 66.9 mm
ScouseTom_Shield
PCB - Arduino
MicroUSB B - Hirose - ZX62D-B-5P8
MicroUSB AB - Hirose - ZX62D-AB-5P8
Power Jack - Kycon - KLDHCX-0202-A
Berg Header Receptacle 2.54 x 8 - FCI - 66951-008LF x 5
Berg Header Receptacle 2.54 x 10 - FCI - 66951-010LF
Berg Header Receptacle 2.54 x 36 - FCI - 66953-018LF
Switch - ESwitch - TLE3303
ScouseTom_Case

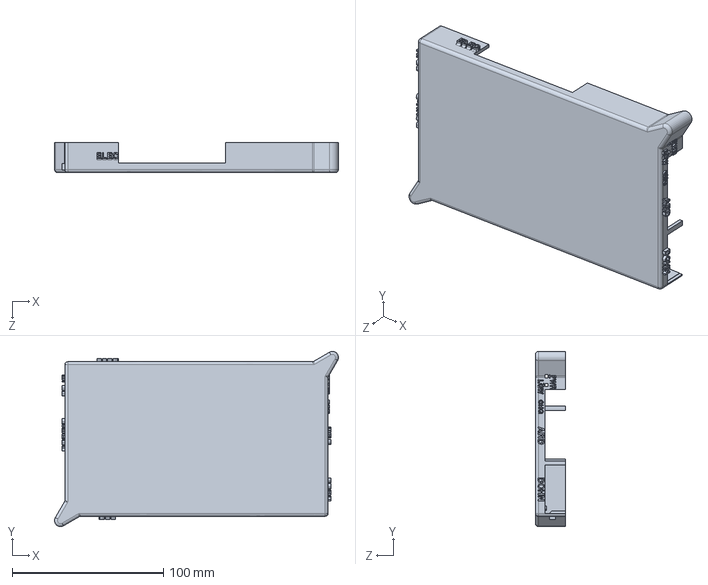
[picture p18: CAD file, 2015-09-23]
doc/case/SwitchBoardCase - Main.sldprt
187.9 x 115.9 x 20.0 mm

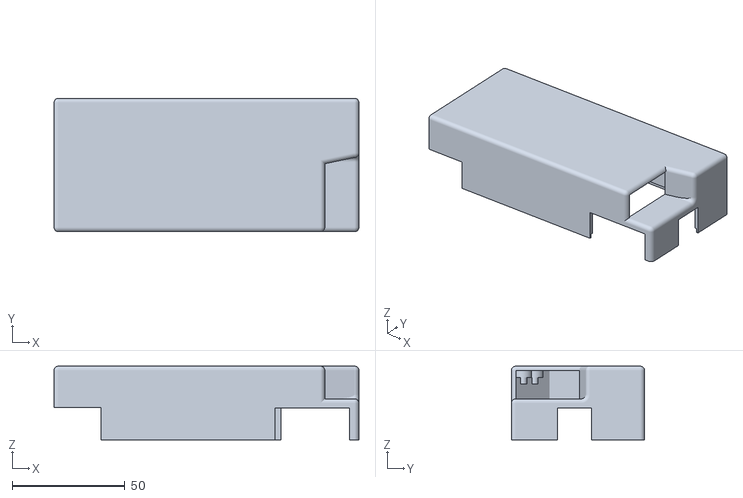
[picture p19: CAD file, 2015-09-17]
doc/case/ScouseTomCasePrintMain.STL
135.3 x 59.2 x 32.7

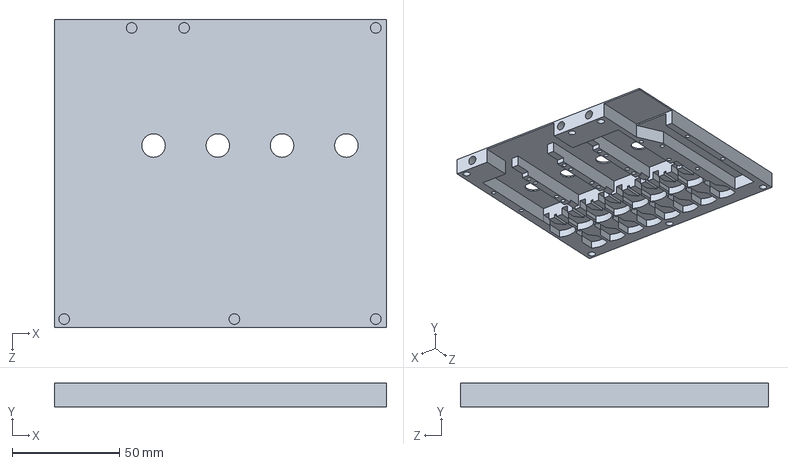
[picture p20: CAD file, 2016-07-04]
doc/Actichamp holder/connector_base_B.SLDPRT
155.0 x 11.0 x 143.9 mm

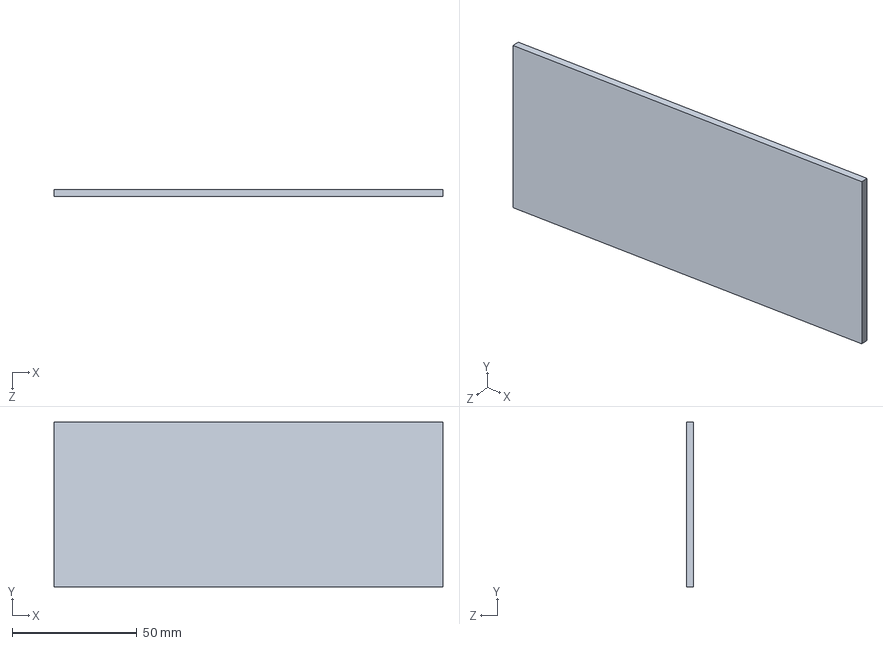
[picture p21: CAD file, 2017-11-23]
doc/ActiChamp_Simple_Box/Actichamp_box_back.SLDPRT
156.0 x 66.0 x 3.00 mm

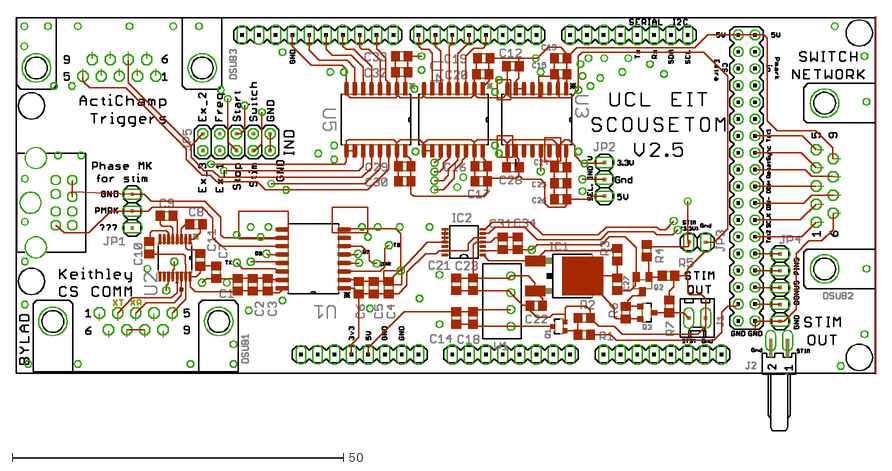
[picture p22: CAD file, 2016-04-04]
doc/figures/Components/ScouseTom_New.dxf
129.8 x 62.5

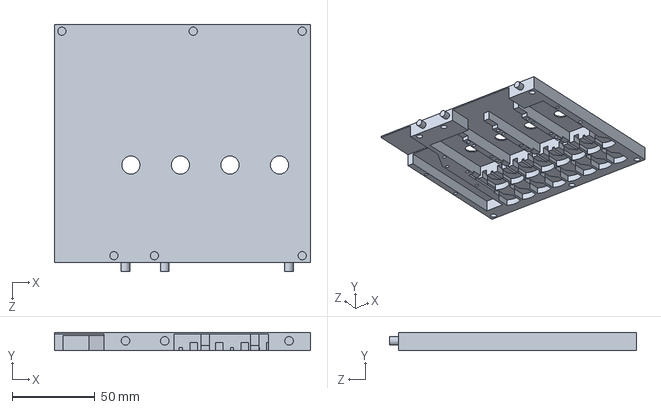
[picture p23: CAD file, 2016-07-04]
doc/Actichamp holder/connector_base_A.SLDPRT
155.0 x 11.0 x 149.4 mm

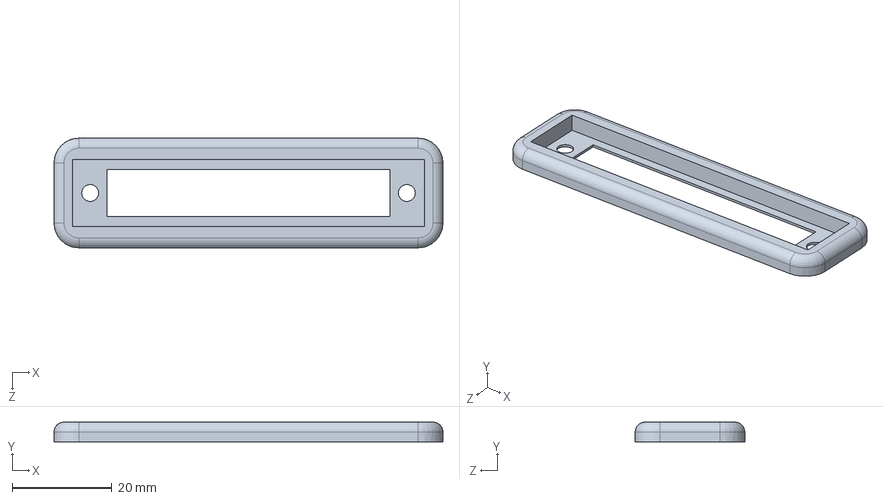
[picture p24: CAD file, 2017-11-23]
doc/case/Dsub_Gasket.SLDPRT
78.0 x 4.00 x 22.0 mm

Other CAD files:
doc/case/Arduino Due/MicroUSB B - Hirose - ZX62D-B-5P8.sldprt
doc/case/Arduino Due/MicroUSB AB - Hirose - ZX62D-AB-5P8.sldprt
doc/figures/Components/SwitchBoard.dxf
doc/Actichamp holder/support.SLDPRT
doc/ActiChamp_Simple_Box/Actichamp_box_Side.SLDPRT
doc/ActiChamp_Simple_Box/Actichamp_box_base.SLDPRT
doc/case/Arduino Due/Berg Header Receptacle 2.54 x 10 - FCI - 66951-010LF.sldprt
doc/case/Arduino Due/Berg Header Receptacle 2.54 x 36 - FCI - 66953-018LF.sldprt
doc/case/Arduino Due/Berg Header Receptacle 2.54 x 8 - FCI - 66951-008LF.sldprt
doc/case/Arduino Due/PCB - Arduino.sldprt
doc/case/Arduino Due/Power Jack - Kycon - KLDHCX-0202-A.sldprt
doc/case/Arduino Due/Switch - ESwitch - TLE3303.sldprt
doc/case/Dsub2Croc.SLDPRT
doc/case/Dsub2CrocCase.SLDPRT
doc/case/Dsub2CrocCase.STL
doc/case/Dsub2CrocPrintingAlignment.SLDPRT
doc/case/Dsub2CrocPrintingLid.STL
doc/case/DsubCover.SLDPRT
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

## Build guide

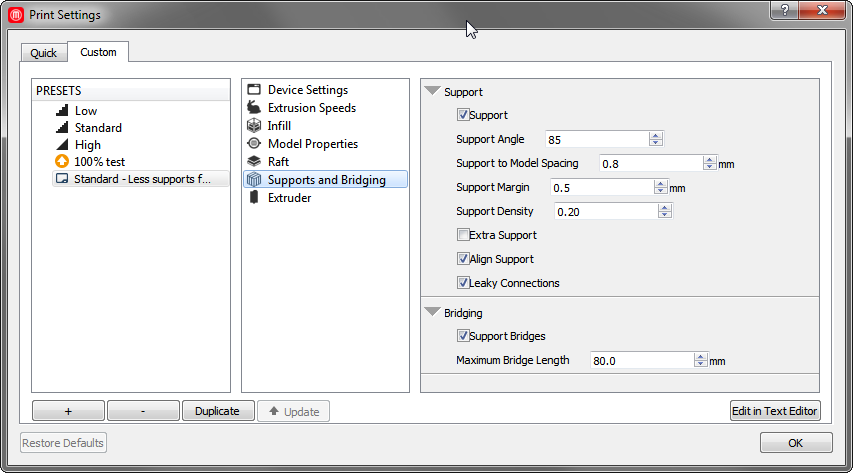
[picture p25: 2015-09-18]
doc/case/ScouseTomShieldPrintSettings.png

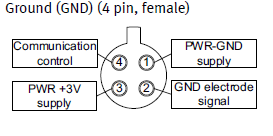
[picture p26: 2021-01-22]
doc/ActiChamp/GroundPinWiring.png

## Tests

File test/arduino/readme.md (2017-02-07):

#Arduino Test code
Arduino sketches which can be uploaded to ScouseTom controller to test components are working individually.

This will likely change a lot when we go through the steps!

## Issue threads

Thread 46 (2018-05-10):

### ISSUE TITLE
EIT project

### ISSUE THREAD

**Issue by oxes500** [EIT-team/ScouseTom#46]
Hello, i would like to ask you, is it possible to use your codes to make arduino EIT device. I'm studying biomedical engineering in my project i need to make it. So could you be so king to explain how it would be possible and what i need.

Thank you.
I look forward to hearing from you.

**Comment by Jimbles** [comment]
Hey,
Yes everything is inside the repository. The checklist in the readme details what you will need

* Two commercial components *
- [Keithley 6221](http://www.tek.com/keithley-low-level-sensitive-and-specialty-instruments/keithley-ultra-sensitive-current-sources-seri) Current source
- EEG system with sufficient bandwidth. The [Biosemi](http://www.biosemi.com/) and  [actiCHamp](http://www.brainvision.com/actichamp.html0) have been used so far, and likely the [gtec](http://www.gtec.at/) or the [Open-Ephys](http://www.open-ephys.org/) will work too

* Custom PCBs and an arduino *
- [Arduino Due](https://www.arduino.cc/en/Main/arduinoBoardDue) For the controller
- [Arduino Switch Board](./src/schematics/Ard_Shield) This controls the current source and the timing of switching current injection pairs
- [Switch Network](./src/schematics/ScouseTom_SwitchNetwork) At least one, each for 37 channels. This connects the current source to the EEG system and the electrodes

This system is primarily aimed at research, and is thus not the cheapest system. If you wanted the lowest cost complete EIT system, then its probably the [SwissTom Pioneer Set](http://www.swisstom.com/en/products/pioneer-set)

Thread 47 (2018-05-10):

### ISSUE TITLE
ScouseTom Operating Query

### ISSUE THREAD

**Issue by twilliams6** [EIT-team/ScouseTom#47]
Hello,

I tried to email yourselves with my query to the email given (medphys.eit-group@ucl.ac.uk), but unfortunately it appears that my email was denied as you only seem to be able to accept messages from people in your organisation.

So I will post my query below instead.

Dear Sir/Madam,

I am a PhD student at Loughborough University and am interested in making a ScouseTom system. I was wondering what frequency and current you ran your system when testing phantoms etc? You state the range in which it can potentially operate, but not any specific information on what state you used to record your experiments.

I am considering a multi-frequency approach and am trying to determine if the ScouseTom system would be a good platform to base my experiments on.

Any advice and guidance that you could give me would be very much appreciated.

Thanks for your time.

**Comment by tdowrick** [comment]
Hi there,

Thanks for your interest and for the info on the e-mail address, we will fix that.

Most of the details should be in the accompanying paper [here](http://www.mdpi.com/1424-8220/17/2/280), sections 2.2.1 and 2.2.2 give details on the resistor phantom experiments, which used 100uA current between 20Hz and 20kHz. For a typical test we would normally use 1 or 2kHz, but that is more force of habit than for any particular reason.

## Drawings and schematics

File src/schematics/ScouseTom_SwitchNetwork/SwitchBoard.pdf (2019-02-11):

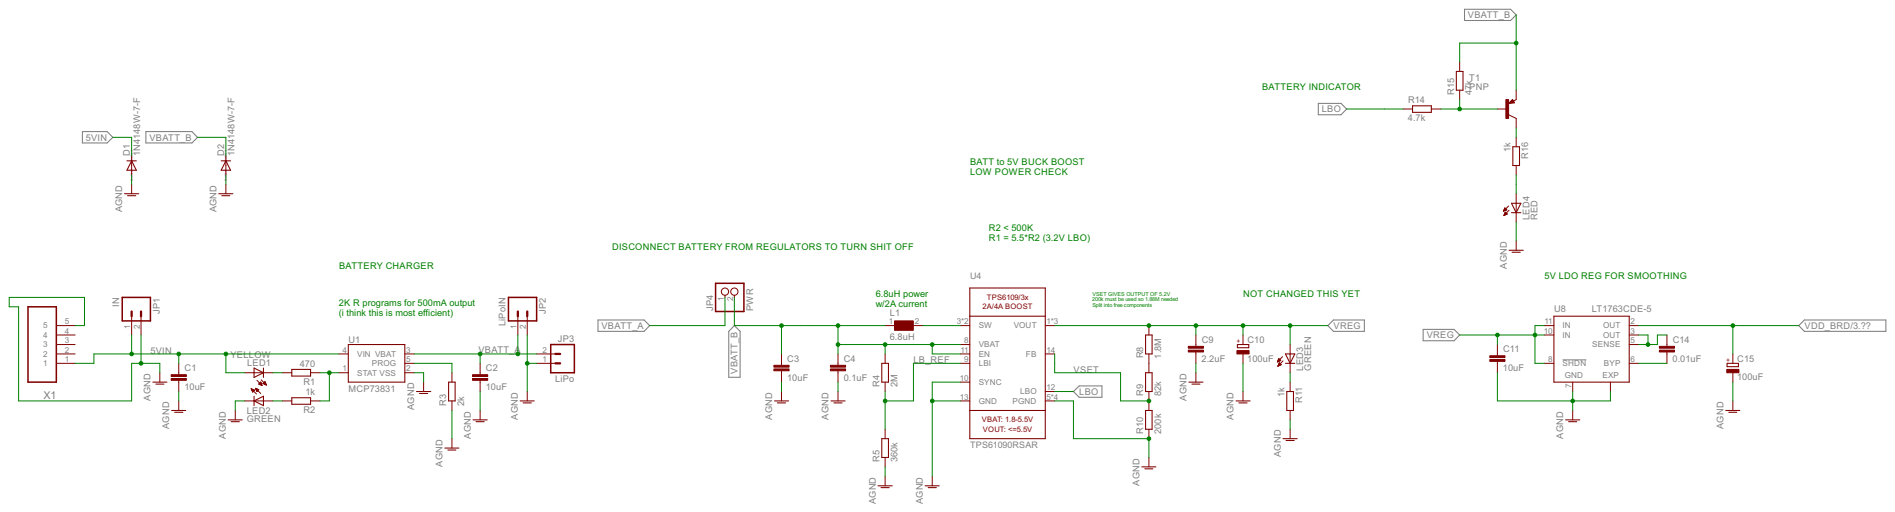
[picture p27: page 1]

SpiceOrder 1 SpiceOrder 2 SpiceOrder 1 SpiceOrder 2 MCP73831 LiPo IN LiPoIN AGND AGNDAGND AGNDAGND LT1763CDE-5 AGND 10uF AGND 0.01uF 10uF 10uF 2k 4701k AGND YELLOW GREEN TPS61090RSAR AGND AGND AGND AGND AGND AGND AGND AGND AGND 2.2uF 10uF 0.1uF 360k 2M 1k 1.8M 200k GREEN 82k 1k RED 6.8uH 100uF 100uF AGND 4.7k 47kPNP PWR 1N4148W-7-F AGND 1N4148W-7-F AGND U1VIN 4 STAT 1 VBAT 3 PROG 5 VSS 2 JP3 12 JP1 12 JP2 12 GND U8 EXP IN 11 OUT 2 SHDN 8 SENSE 5 7 BYP 6 IN 10 OUT 3 C11 C14 C1 C2 R3 R1 R2 LED1 LED2 EN 11 FB 14 GND 13 LBI 9 LBO 12 PGND 5*4 SW 3*2 SYNC 10 VBAT 8 VOUT 1*3 U4 C9 C3 C4 R5 R4 R11 R8 R10 LED3 R9 R16 LED4 L1 1 2 C10 C15 R14 R15T1 JP412 1 1 2 2 3 3 4 4 5 5 X1 D1 D2 5VIN 5VIN VBATT_B VBATT_B VBATT_B VREG VREG LB_REF VSET LBO LBO VBATT_A VBATT_A VDD_BRD/3.?? TPS6109/3x 2A/4A BOOST VBAT: 1.8-5.5V VOUT: <=5.5V + + BATTERY CHARGER BATT to 5V BUCK BOOST LOW POWER CHECK 5V LDO REG FOR SMOOTHING 6.8uH power w/2A current R2 < 500K R1 = 5.5*R2 (3.2V LBO) BATTERY INDICATOR VSET GIVES OUTPUT OF 5.2V 200k must be used so 1.88M needed Split into free components NOT CHANGED THIS YET 2K R programs for 500mA output (i think this is most efficient) DISCONNECT BATTERY FROM REGULATORS TO TURN SHIT OFF

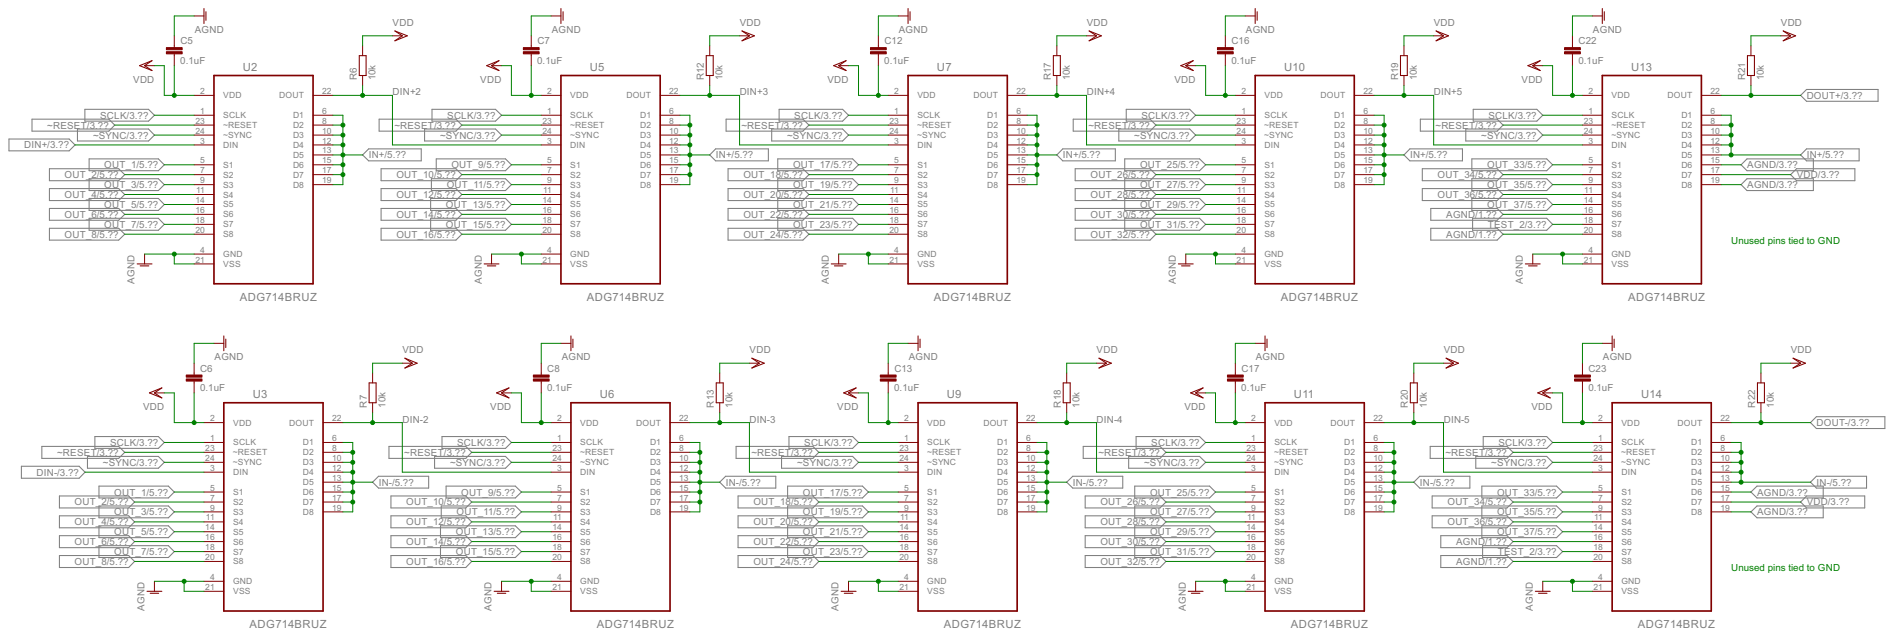
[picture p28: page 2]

AGND/3.?? AGND/3.?? AGND/1.?? AGND/1.??
OUT_34/5.??

Unused pins tied to GND

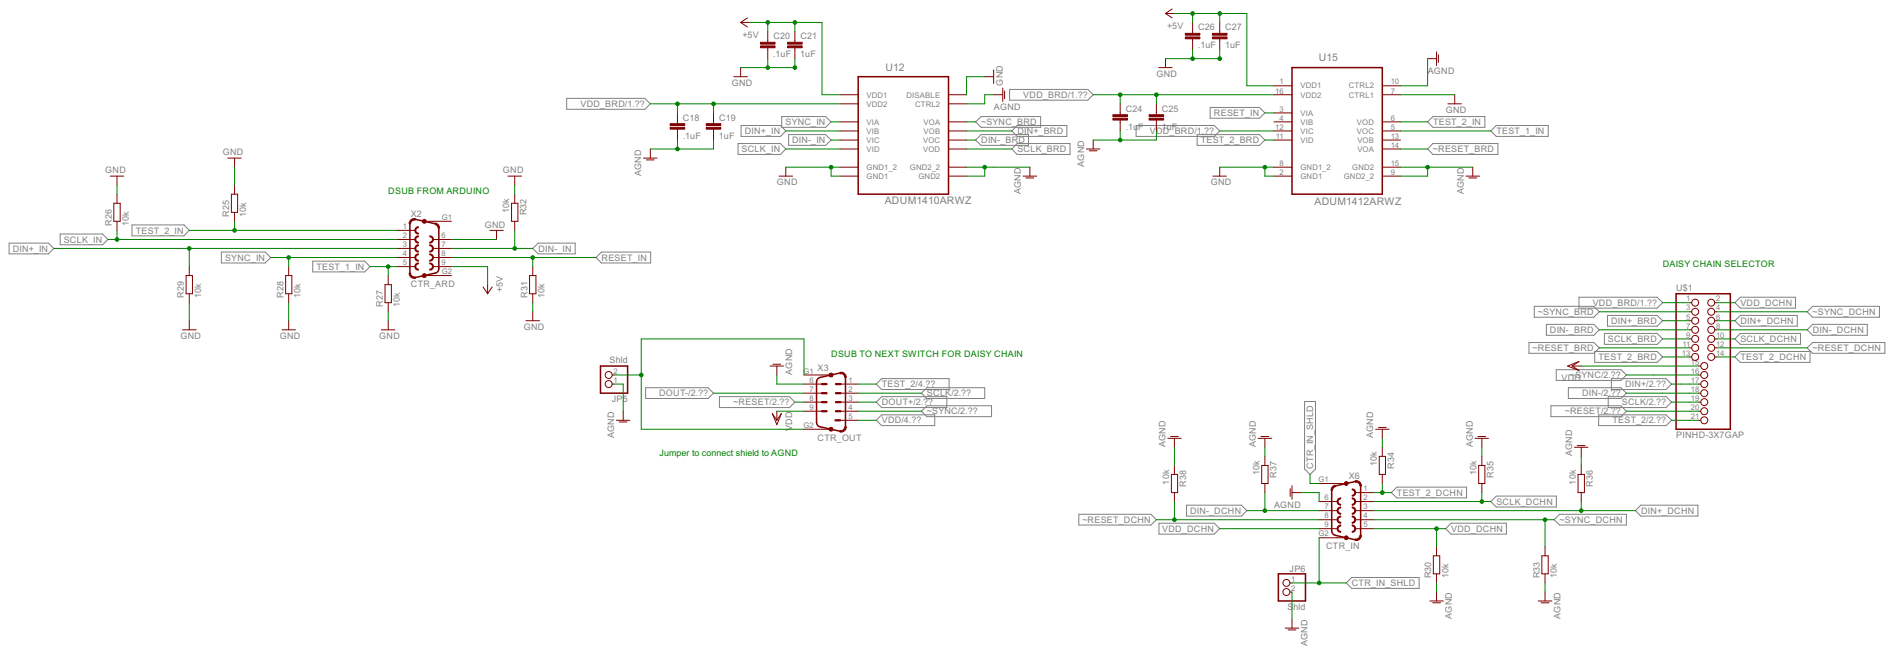
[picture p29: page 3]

SCLK_IN | SCLK_BRD | 15 VOA ~RESET_BRD

DSUB TO NEXT SWITCH FOR DAISY CHAIN

Jumper to connect shield to AGND

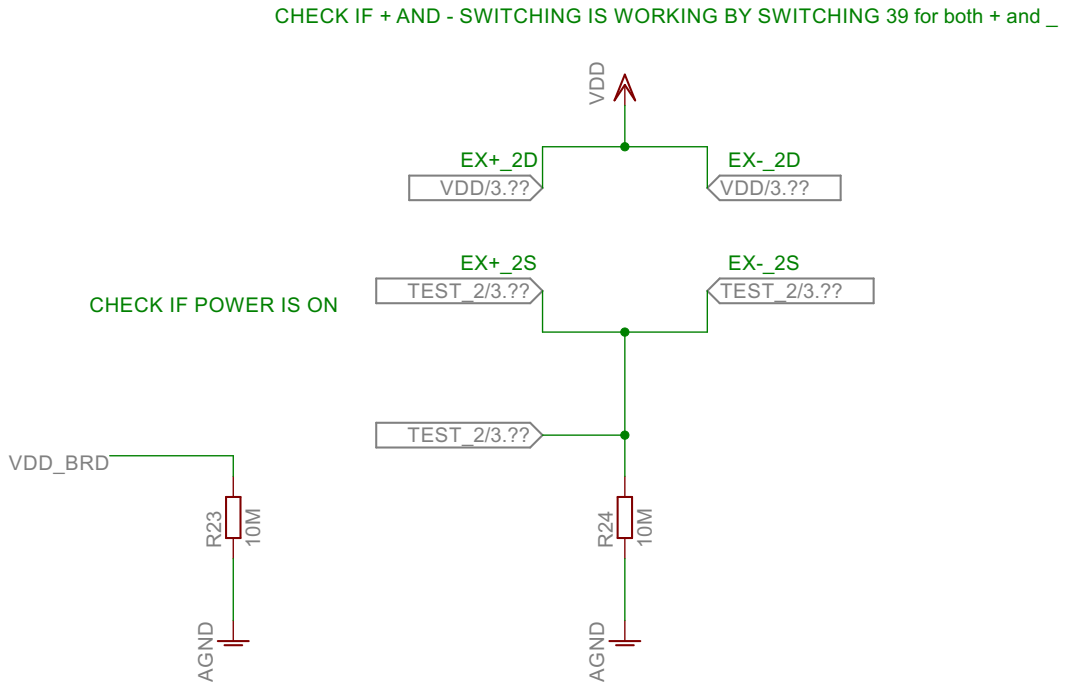
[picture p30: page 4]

CHECK IF + AND - SWITCHING IS WORKING BY SWITCHING 39 for both + and _

CHECK IF POWER IS ON

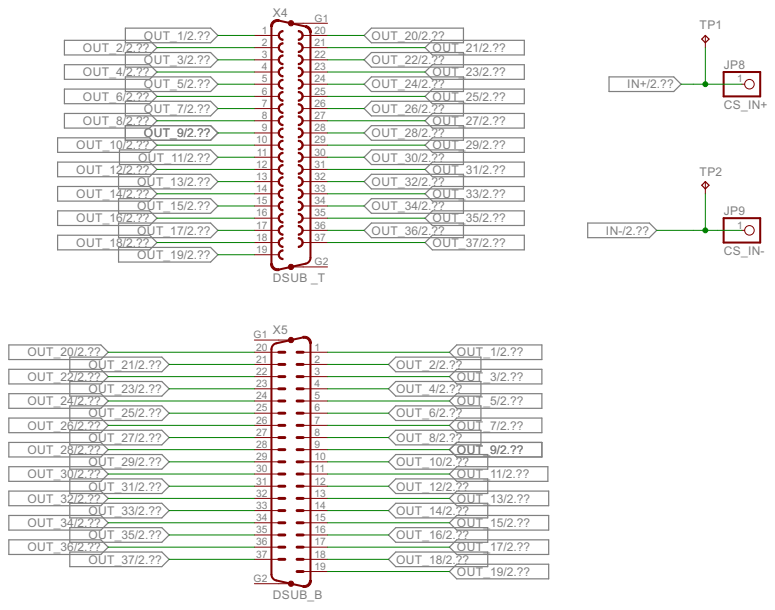
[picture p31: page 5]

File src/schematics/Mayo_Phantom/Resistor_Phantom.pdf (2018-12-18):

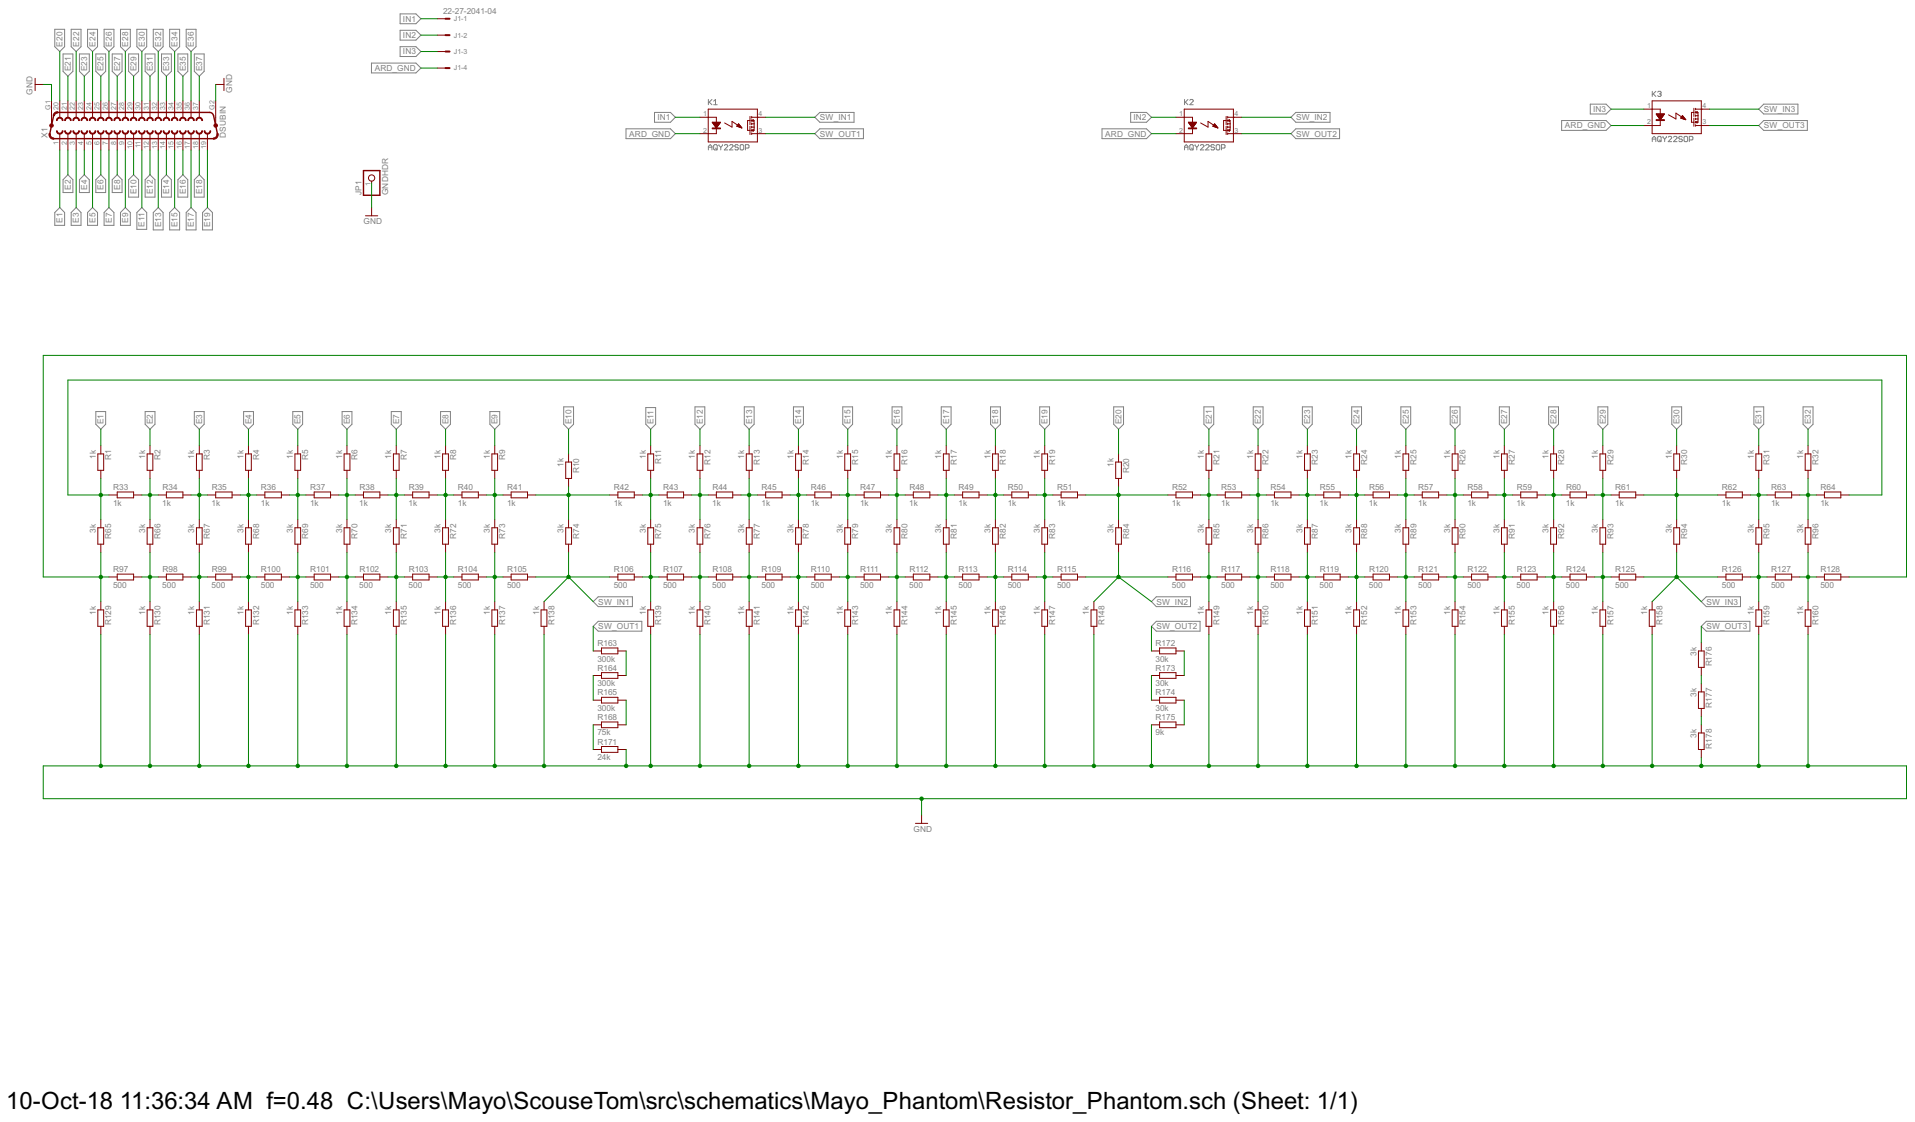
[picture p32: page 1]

10-Oct-18 11:36:34 AM f=0.48 C:\Users\Mayo\ScouseTom\src\schematics\Mayo_Phantom\Resistor_Phantom.sch (Sheet: 1/1)

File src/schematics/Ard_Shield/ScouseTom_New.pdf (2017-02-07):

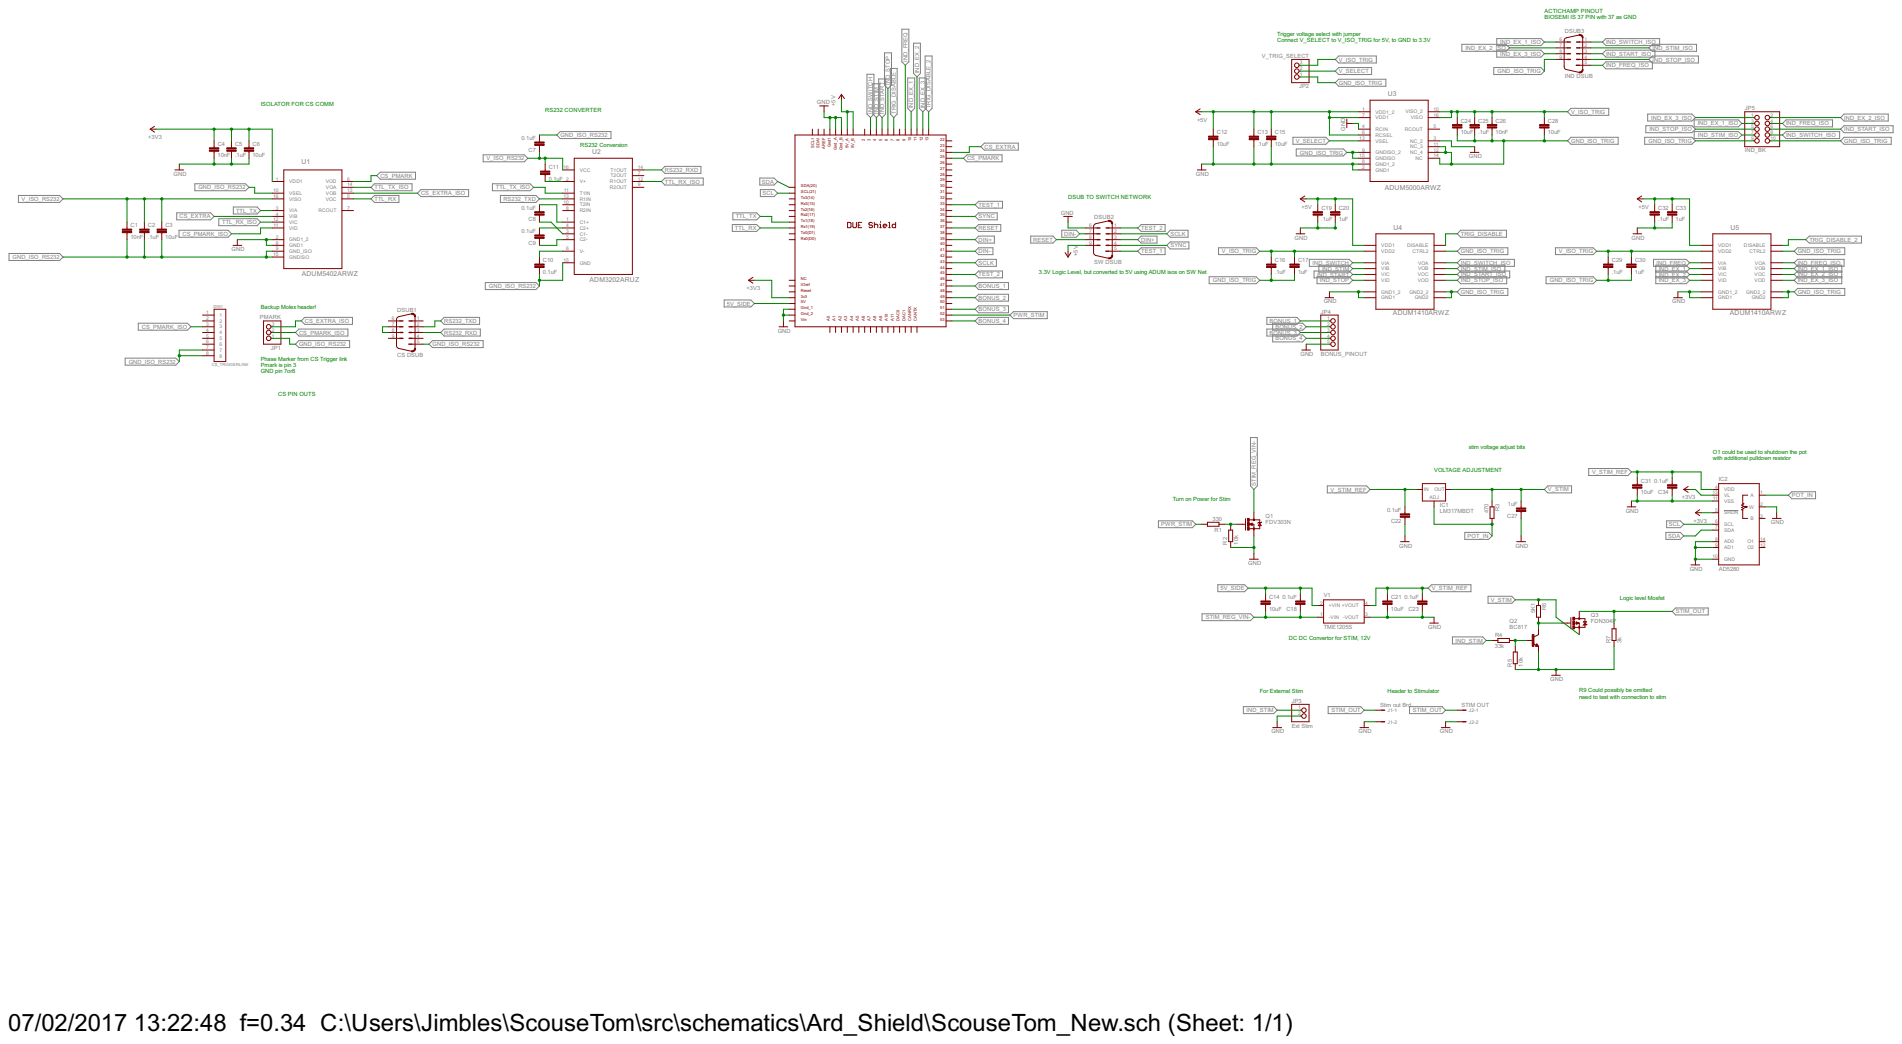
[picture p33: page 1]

ACTICHAMP PINOUT BIOSEMI IS 37 PIN with 37 as GND

Trigger voltage select with jumper Connect V_SELECT to V_ISO_TRIG for 5V, to GND to 3.3V

ISOLATOR FOR CS COMM

DSUB TO SWITCH NETWORK

3.3V Logic Level, but converted to 5V using ADUM isos on SW Net

Phase Marker from CS Trigger link Pmark is pin 3 GND pin 7or8

stim voltage adjust bits

O1 could be used to shutdown the pot with additional pulldown resistor

Turn on Power for Stim

DC DC Convertor for STIM, 12V

need to test with connection to stim

Stim out Brd GND

07/02/2017 13:22:48 f=0.34 C:\Users\Jimbles\ScouseTom\src\schematics\Ard_Shield\ScouseTom_New.sch (Sheet: 1/1)

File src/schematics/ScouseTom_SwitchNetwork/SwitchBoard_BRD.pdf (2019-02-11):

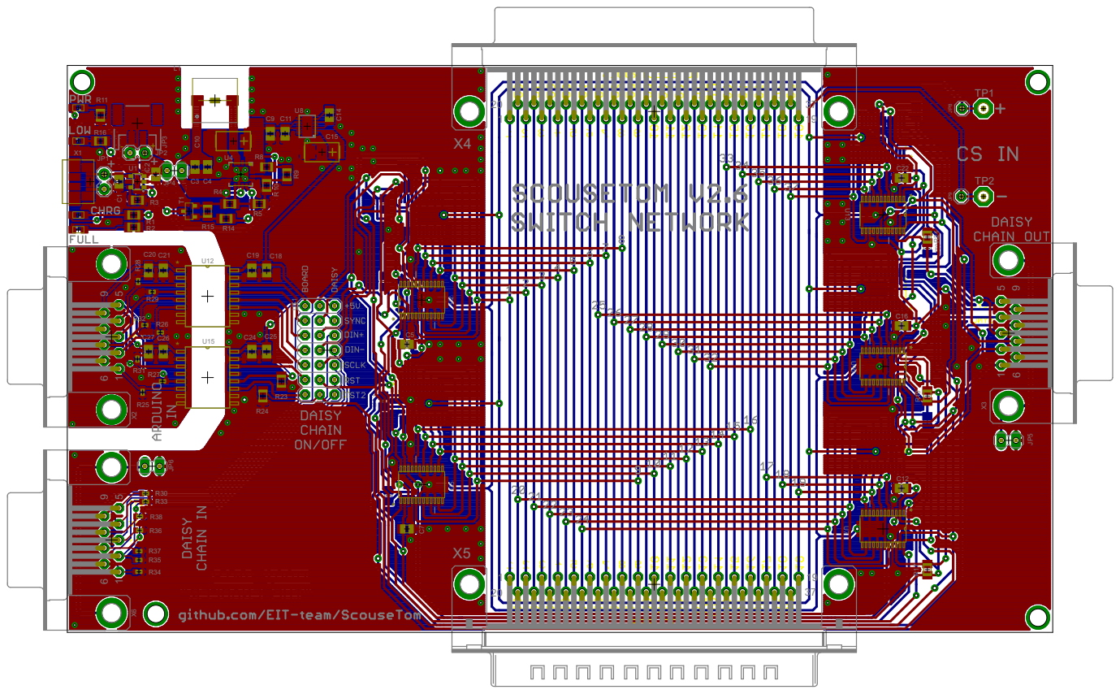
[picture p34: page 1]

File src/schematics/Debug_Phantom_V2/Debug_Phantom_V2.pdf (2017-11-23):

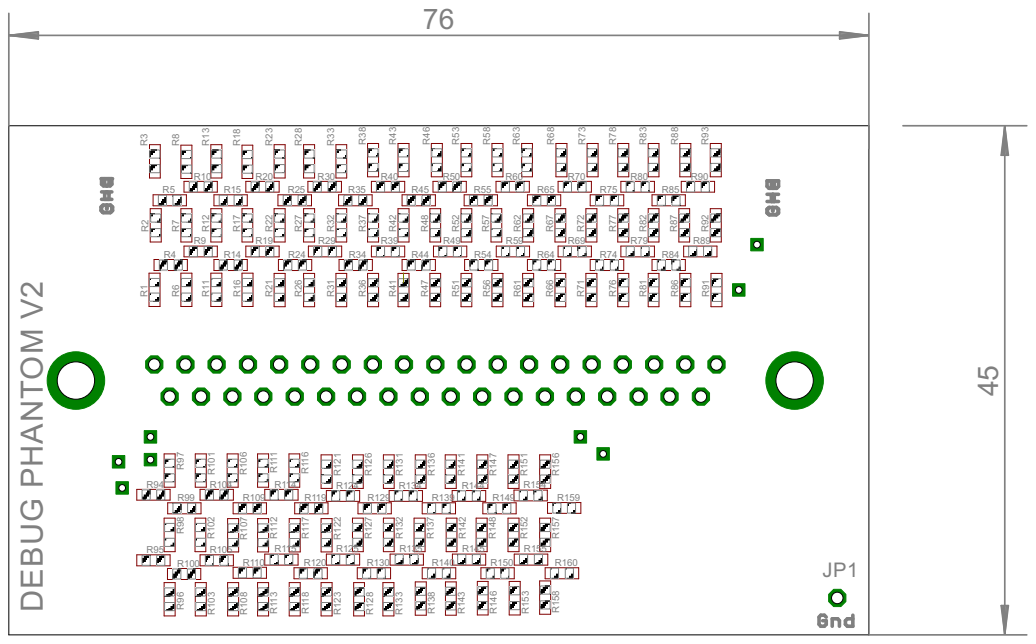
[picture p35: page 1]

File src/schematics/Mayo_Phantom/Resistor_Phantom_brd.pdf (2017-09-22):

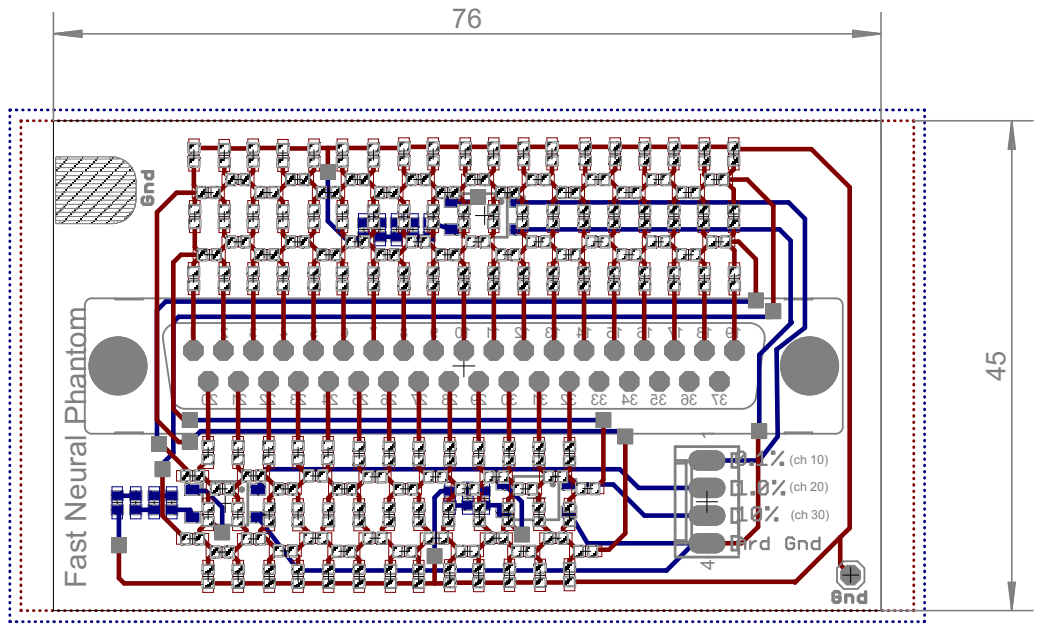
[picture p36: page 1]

(ch 30) Fast Neural Phantom

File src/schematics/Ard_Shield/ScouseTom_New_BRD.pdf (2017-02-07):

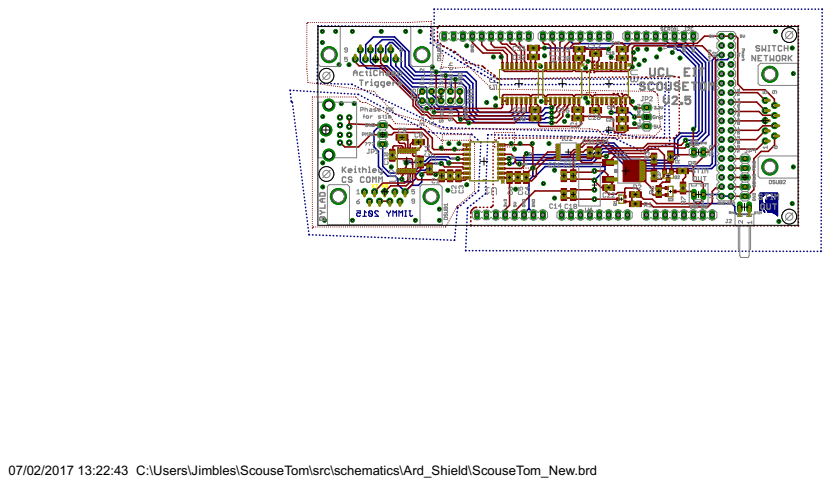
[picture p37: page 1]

07/02/2017 13:22:43 C:\Users\Jimbles\ScouseTom\src\schematics\Ard_Shield\ScouseTom_New.brd

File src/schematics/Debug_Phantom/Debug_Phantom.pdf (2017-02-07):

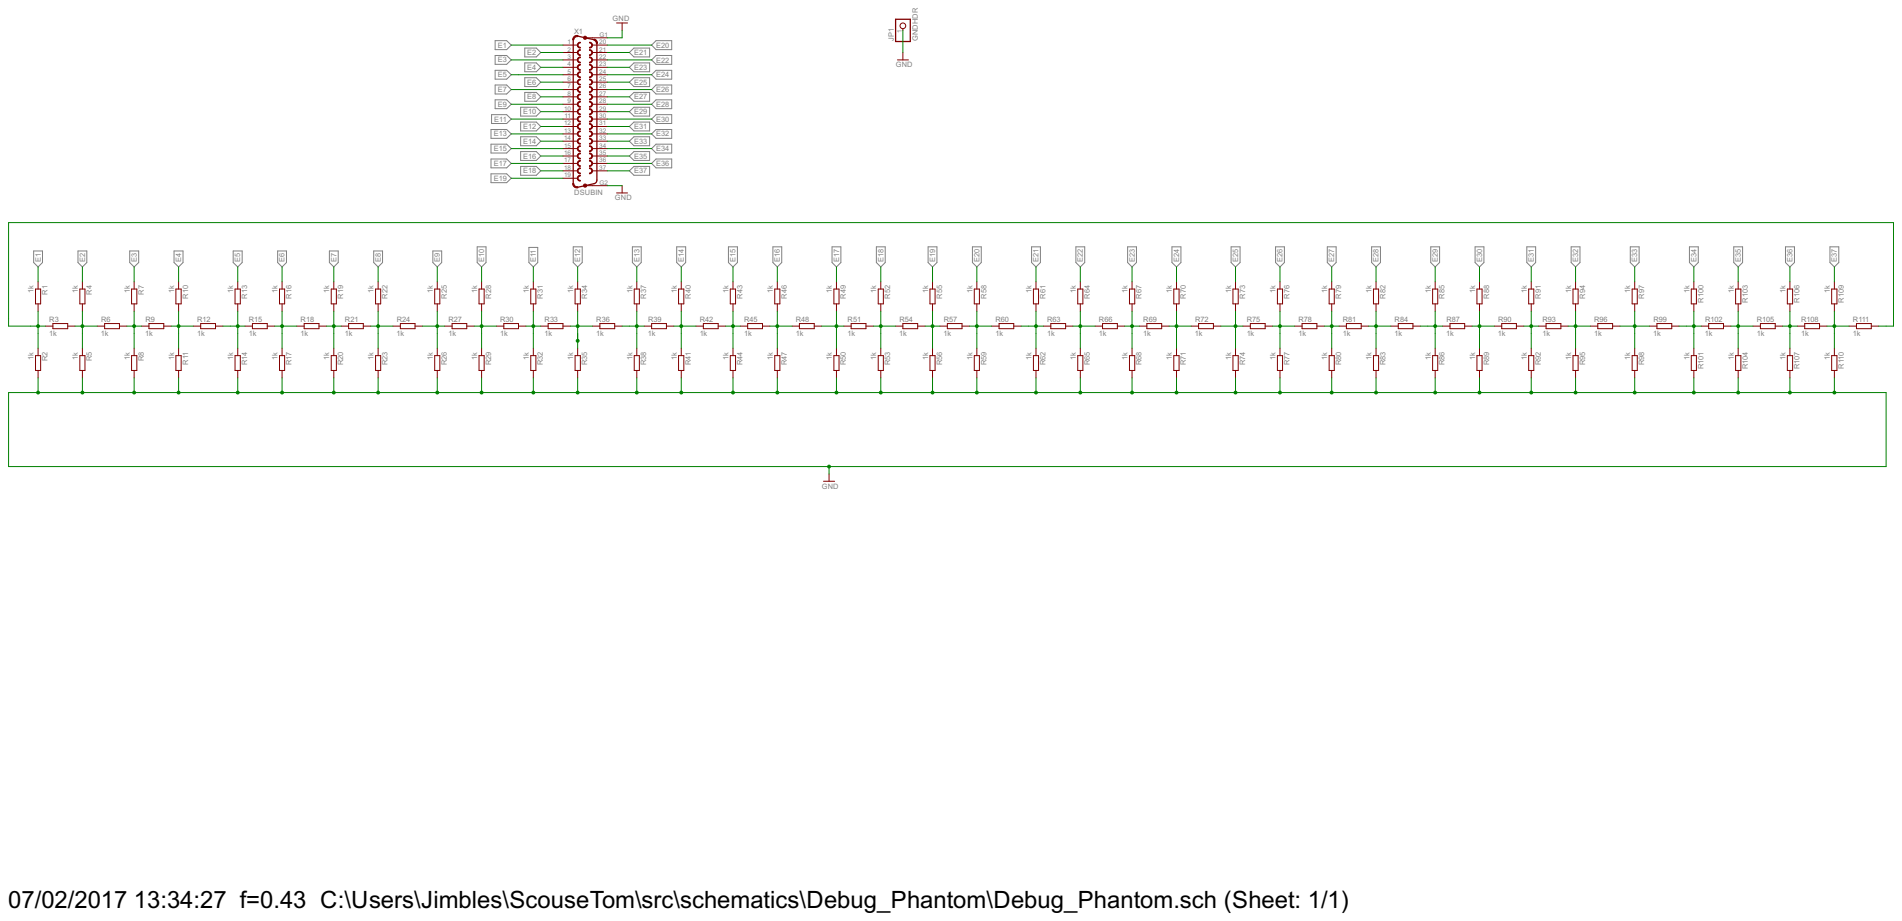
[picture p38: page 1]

07/02/2017 13:34:27 f=0.43 C:\Users\Jimbles\ScouseTom\src\schematics\Debug_Phantom\Debug_Phantom.sch (Sheet: 1/1)

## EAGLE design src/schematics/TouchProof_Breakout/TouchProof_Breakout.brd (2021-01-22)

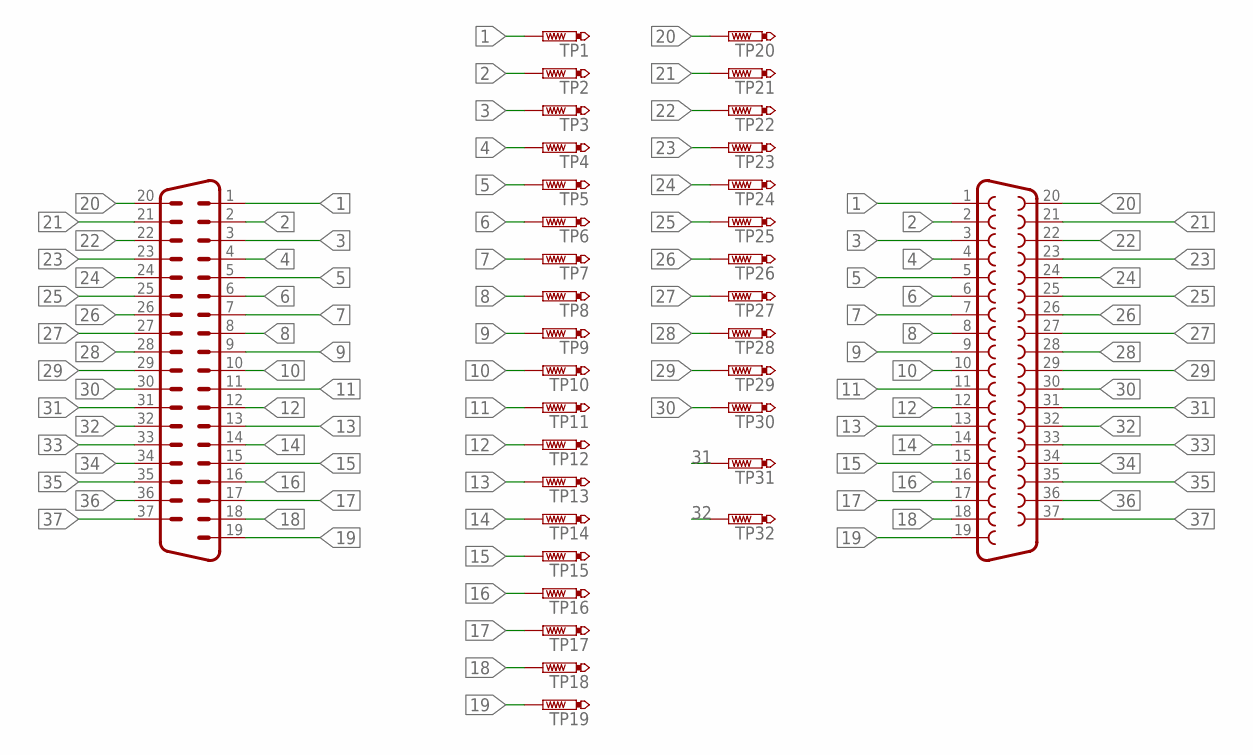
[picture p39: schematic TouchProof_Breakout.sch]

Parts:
TP1, TP2, TP3, TP4, TP5, TP6, TP7, TP8, TP9, TP10, TP11, TP12, TP13, TP14, TP15, TP16, TP17, TP18, TP19, TP20, TP21, TP22, TP23, TP24, TP25, TP26, TP27, TP28, TP29, TP30, TP31, TP32: TOUCHPROOF; TOUCHPROOF_PIN
X40: M37HP
X41: F37HP

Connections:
1: TP1.TP, X40.1, X41.1
2: TP2.TP, X40.2, X41.2
3: TP3.TP, X40.3, X41.3
4: TP4.TP, X40.4, X41.4
5: TP5.TP, X40.5, X41.5
6: TP6.TP, X40.6, X41.6
7: TP7.TP, X40.7, X41.7
8: TP8.TP, X40.8, X41.8
9: TP9.TP, X40.9, X41.9
10: TP10.TP, X40.10, X41.10
11: TP11.TP, X40.11, X41.11
12: TP12.TP, X40.12, X41.12
13: TP13.TP, X40.13, X41.13
14: TP14.TP, X40.14, X41.14
15: TP15.TP, X40.15, X41.15
16: TP16.TP, X40.16, X41.16
17: TP17.TP, X40.17, X41.17
18: TP18.TP, X40.18, X41.18
19: TP19.TP, X40.19, X41.19
20: TP20.TP, X40.20, X41.20
21: TP21.TP, X40.21, X41.21
22: TP22.TP, X40.22, X41.22
23: TP23.TP, X40.23, X41.23
24: TP24.TP, X40.24, X41.24
25: TP25.TP, X40.25, X41.25
26: TP26.TP, X40.26, X41.26
27: TP27.TP, X40.27, X41.27
28: TP28.TP, X40.28, X41.28
29: TP29.TP, X40.29, X41.29
30: TP30.TP, X40.30, X41.30
31: TP31.TP, X40.31, X41.31
32: TP32.TP, X40.32, X41.32
33: X40.33, X41.33
34: X40.34, X41.34
35: X40.35, X41.35
36: X40.36, X41.36
37: X40.37, X41.37

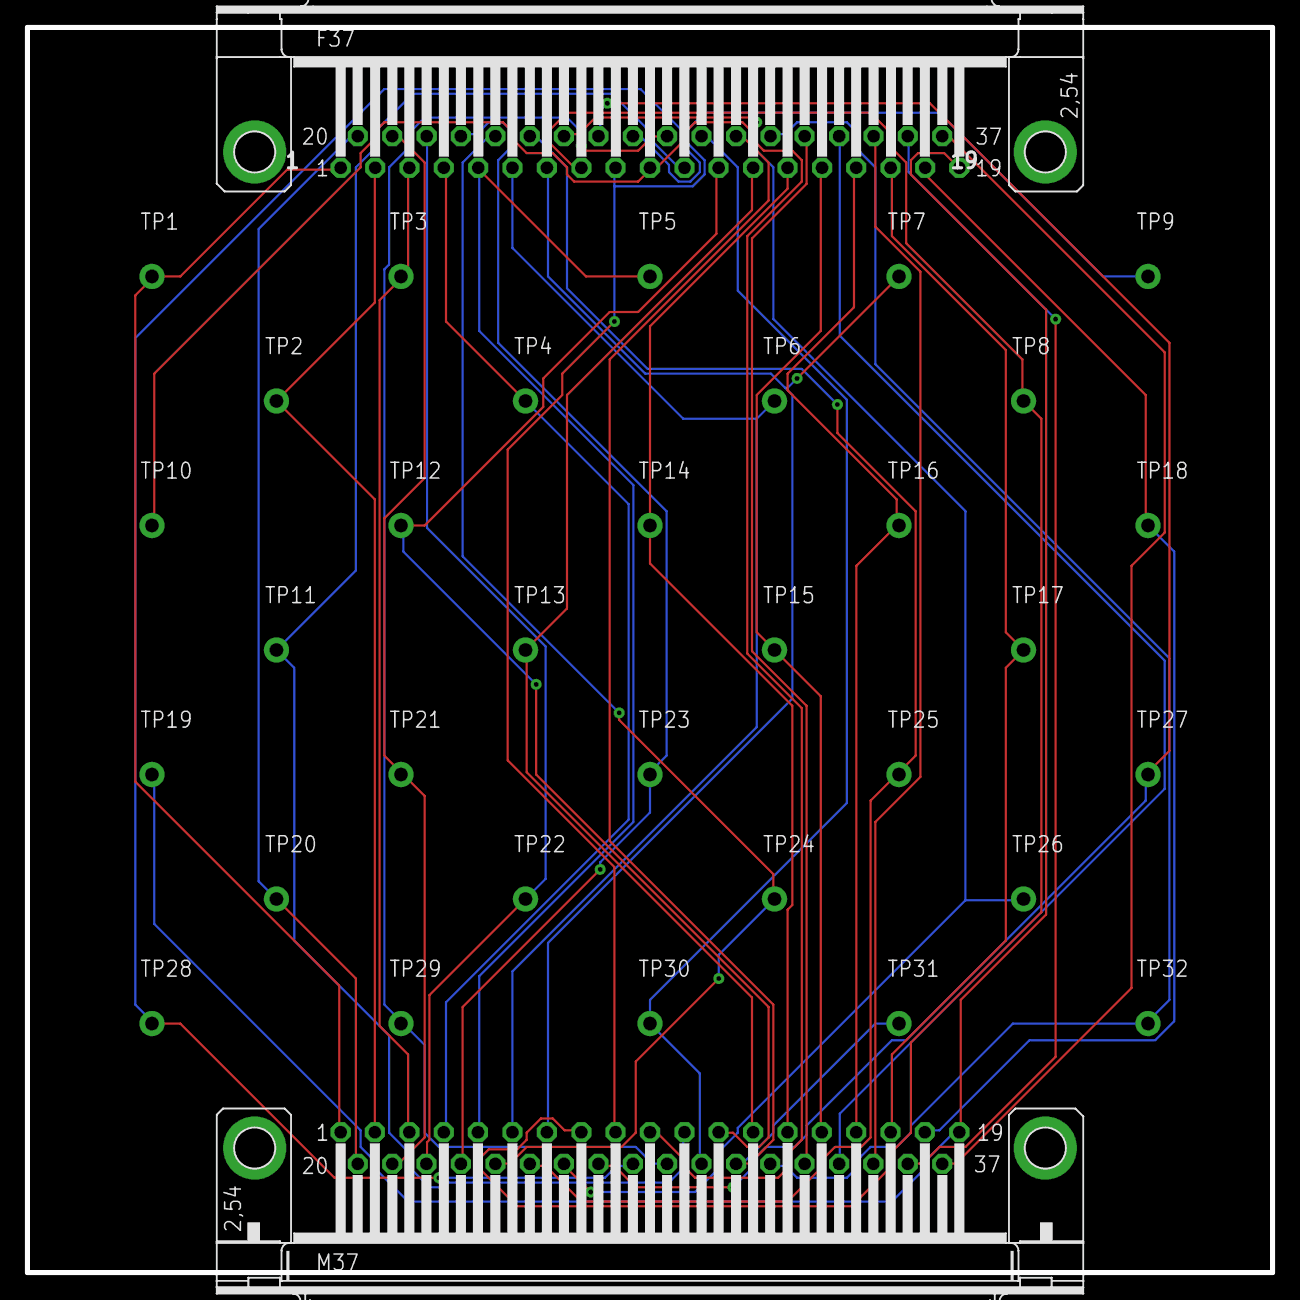
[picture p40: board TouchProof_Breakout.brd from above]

Board: 2 copper layers, 100.0 x 100.0 mm, 34 parts (0 on the bottom side), 37 nets.

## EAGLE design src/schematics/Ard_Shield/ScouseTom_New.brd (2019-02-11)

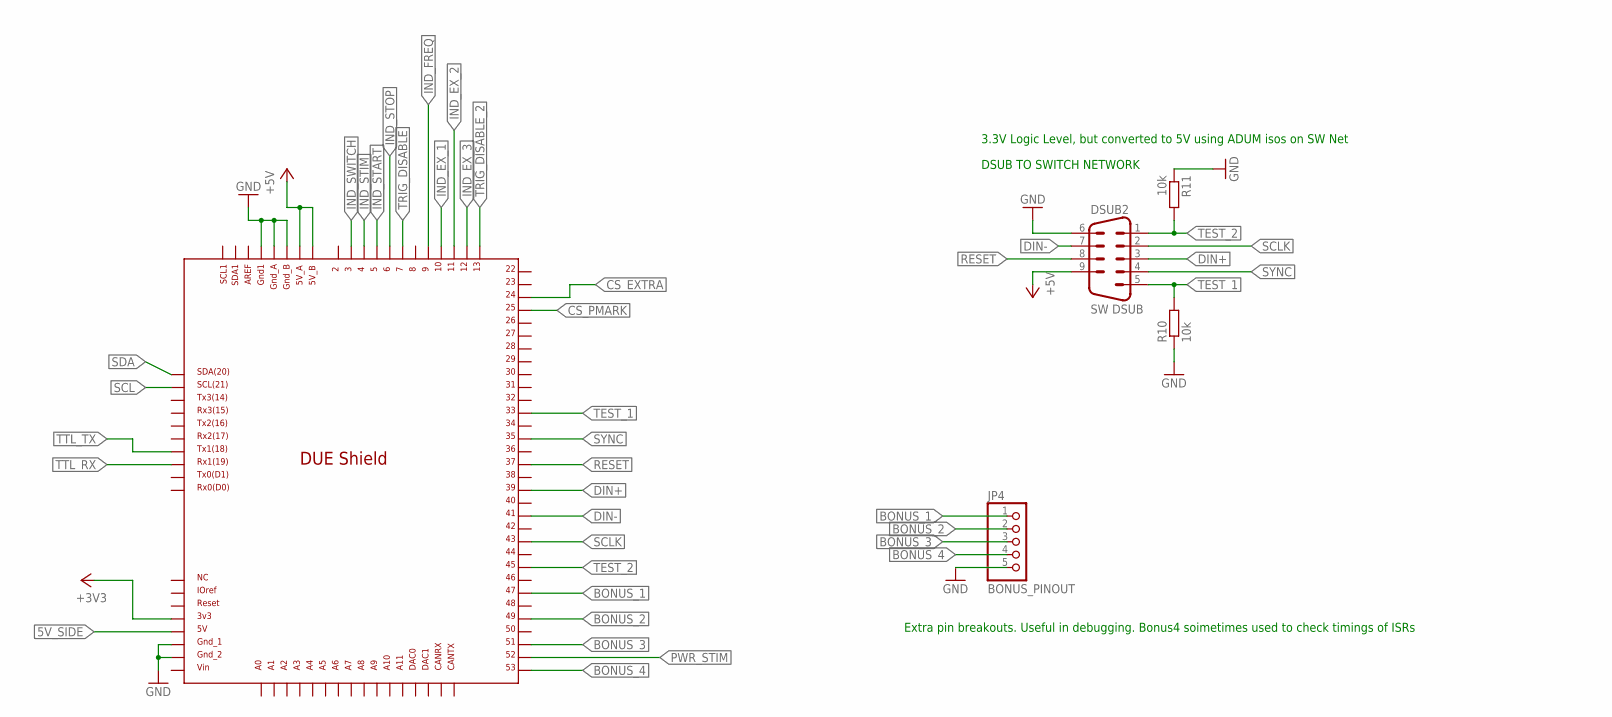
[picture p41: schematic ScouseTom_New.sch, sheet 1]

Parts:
ARD1: DUE(NOMID)
DSUB2: SW DSUB; DSUB9
JP4: BONUS_PINOUT; 1X05
R10, R11: 10k; R0805

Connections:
5V_SIDE: ARD1.5V; also elsewhere on the board
+3V3: ARD1.3V3; also elsewhere on the board
+5V: ARD1.5V_A, ARD1.5V_B, DSUB2.9; also elsewhere on the board
BONUS_1: ARD1.47, JP4.1
BONUS_2: ARD1.49, JP4.2
BONUS_3: ARD1.51, JP4.3
BONUS_4: ARD1.53, JP4.4
CS_EXTRA: ARD1.24; also elsewhere on the board
CS_PMARK: ARD1.25; also elsewhere on the board
DIN+: ARD1.39, DSUB2.3
DIN-: ARD1.41, DSUB2.7
GND: ARD1.GND1, ARD1.GND_1, ARD1.GND_2, ARD1.GND_A, ARD1.GND_B, DSUB2.6, JP4.5, R10.1, R11.1; also elsewhere on the board
IND_EX_1: ARD1.10; also elsewhere on the board
IND_EX_2: ARD1.11; also elsewhere on the board
IND_EX_3: ARD1.12; also elsewhere on the board
IND_FREQ: ARD1.9; also elsewhere on the board
IND_START: ARD1.5; also elsewhere on the board
IND_STIM: ARD1.4; also elsewhere on the board
IND_STOP: ARD1.6; also elsewhere on the board
IND_SWITCH: ARD1.3; also elsewhere on the board
PWR_STIM: ARD1.52; also elsewhere on the board
RESET: ARD1.37, DSUB2.8
SCL: ARD1.SCL; also elsewhere on the board
SCLK: ARD1.43, DSUB2.2
SDA: ARD1.SDA; also elsewhere on the board
SYNC: ARD1.35, DSUB2.4
TEST_1: ARD1.33, DSUB2.5, R10.2
TEST_2: ARD1.45, DSUB2.1, R11.2
TRIG_DISABLE: ARD1.7; also elsewhere on the board
TRIG_DISABLE_2: ARD1.13; also elsewhere on the board
TTL_RX: ARD1.RX1; also elsewhere on the board
TTL_TX: ARD1.TX1; also elsewhere on the board

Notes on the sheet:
DSUB TO SWITCH NETWORK
3.3V Logic Level, but converted to 5V using ADUM isos on SW Net
Extra pin breakouts. Useful in debugging. Bonus4 soimetimes used to check timings of ISRs

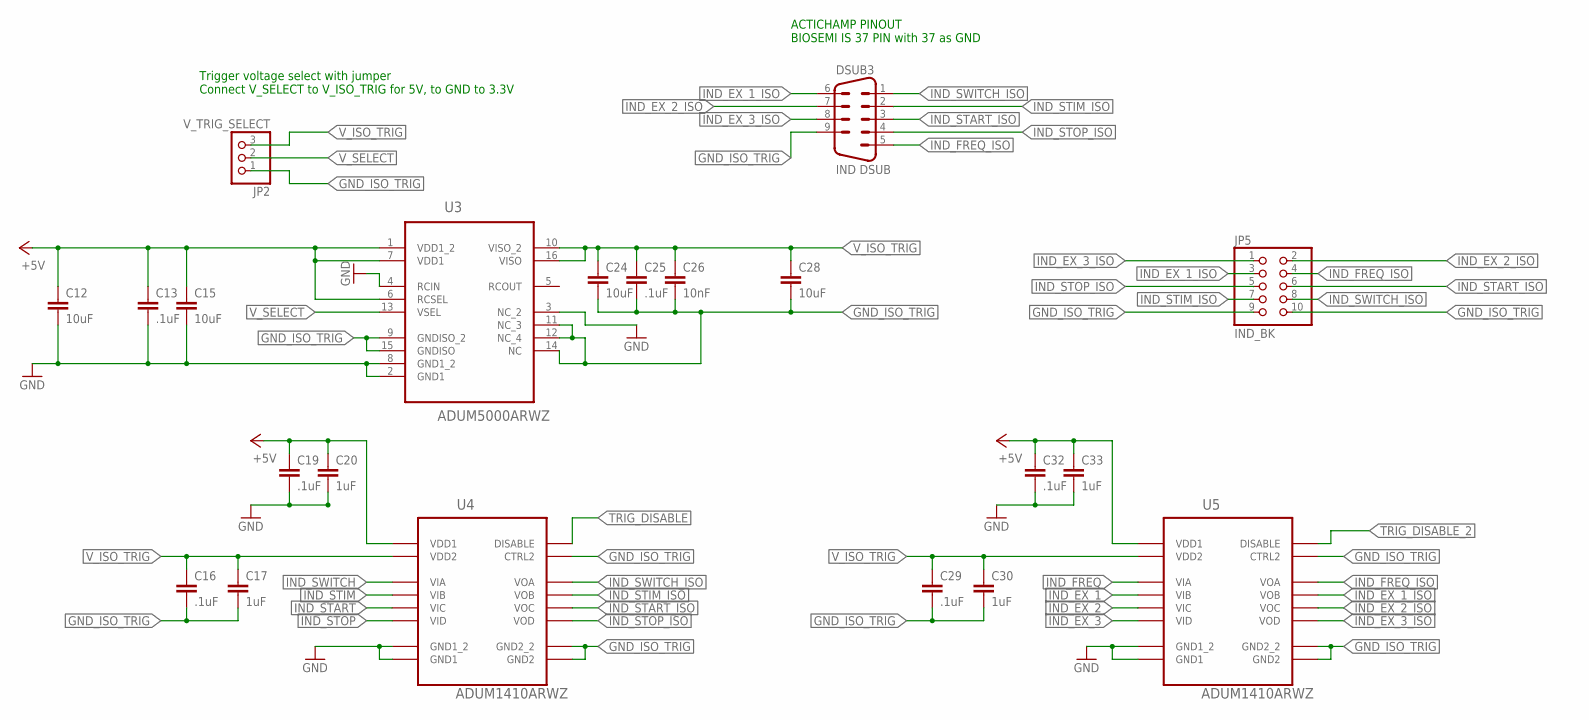
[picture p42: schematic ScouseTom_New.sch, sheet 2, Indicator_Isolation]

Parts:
C12, C15, C24, C28: 10uF; C0805
C13, C16, C19, C25, C29, C32: .1uF; C0805
C17, C20, C30, C33: 1uF; C0805
C26: 10nF; C0805
DSUB3: IND DSUB; DSUB9
JP2: V_TRIG_SELECT; 1X03
JP5: IND_BK; 2X05
U3: ADUM5000ARWZ; SOIC127P1032X265-16N
U4, U5: ADUM1410ARWZ; SOIC127P1032X265-16N

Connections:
+5V: C12.1, C13.1, C15.1, C19.1, C20.1, C32.1, C33.1, U3.1 (VDD1_2), U3.6 (RCSEL), U3.7 (VDD1), U4.1 (VDD1), U5.1 (VDD1); also elsewhere on the board
GND: C12.2, C13.2, C15.2, C19.2, C20.2, C32.2, C33.2, U3.2 (GND1), U3.3 (NC_2), U3.4 (RCIN), U3.8 (GND1_2), U4.2 (GND1_2), U4.8 (GND1), U5.2 (GND1_2), U5.8 (GND1); also elsewhere on the board
GND_ISO_TRIG: C16.2, C17.2, C24.2, C25.2, C26.2, C28.2, C29.2, C30.2, DSUB3.9, JP2.1, JP5.9, JP5.10, U3.9 (GNDISO_2), U3.11 (NC_3), U3.12 (NC_4), U3.14 (NC), U3.15 (GNDISO), U4.9 (GND2_2), U4.10 (CTRL2), U4.15 (GND2), U5.9 (GND2_2), U5.10 (CTRL2), U5.15 (GND2)
IND_EX_1: U5.4 (VIB); also elsewhere on the board
IND_EX_1_ISO: DSUB3.6, JP5.3, U5.13 (VOB)
IND_EX_2: U5.5 (VIC); also elsewhere on the board
IND_EX_2_ISO: DSUB3.7, JP5.2, U5.12 (VOC)
IND_EX_3: U5.6 (VID); also elsewhere on the board
IND_EX_3_ISO: DSUB3.8, JP5.1, U5.11 (VOD)
IND_FREQ: U5.3 (VIA); also elsewhere on the board
IND_FREQ_ISO: DSUB3.5, JP5.4, U5.14 (VOA)
IND_START: U4.5 (VIC); also elsewhere on the board
IND_START_ISO: DSUB3.3, JP5.6, U4.12 (VOC)
IND_STIM: U4.4 (VIB); also elsewhere on the board
IND_STIM_ISO: DSUB3.2, JP5.7, U4.13 (VOB)
IND_STOP: U4.6 (VID); also elsewhere on the board
IND_STOP_ISO: DSUB3.4, JP5.5, U4.11 (VOD)
IND_SWITCH: U4.3 (VIA); also elsewhere on the board
IND_SWITCH_ISO: DSUB3.1, JP5.8, U4.14 (VOA)
TRIG_DISABLE: U4.7 (DISABLE); also elsewhere on the board
TRIG_DISABLE_2: U5.7 (DISABLE); also elsewhere on the board
V_ISO_TRIG: C16.1, C17.1, C24.1, C25.1, C26.1, C28.1, C29.1, C30.1, JP2.3, U3.10 (VISO_2), U3.16 (VISO), U4.16 (VDD2), U5.16 (VDD2)
V_SELECT: JP2.2, U3.13 (VSEL)

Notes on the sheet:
ACTICHAMP PINOUT BIOSEMI IS 37 PIN with 37 as GND
Trigger voltage select with jumper Connect V_SELECT to V_ISO_TRIG for 5V, to GND to 3.3V

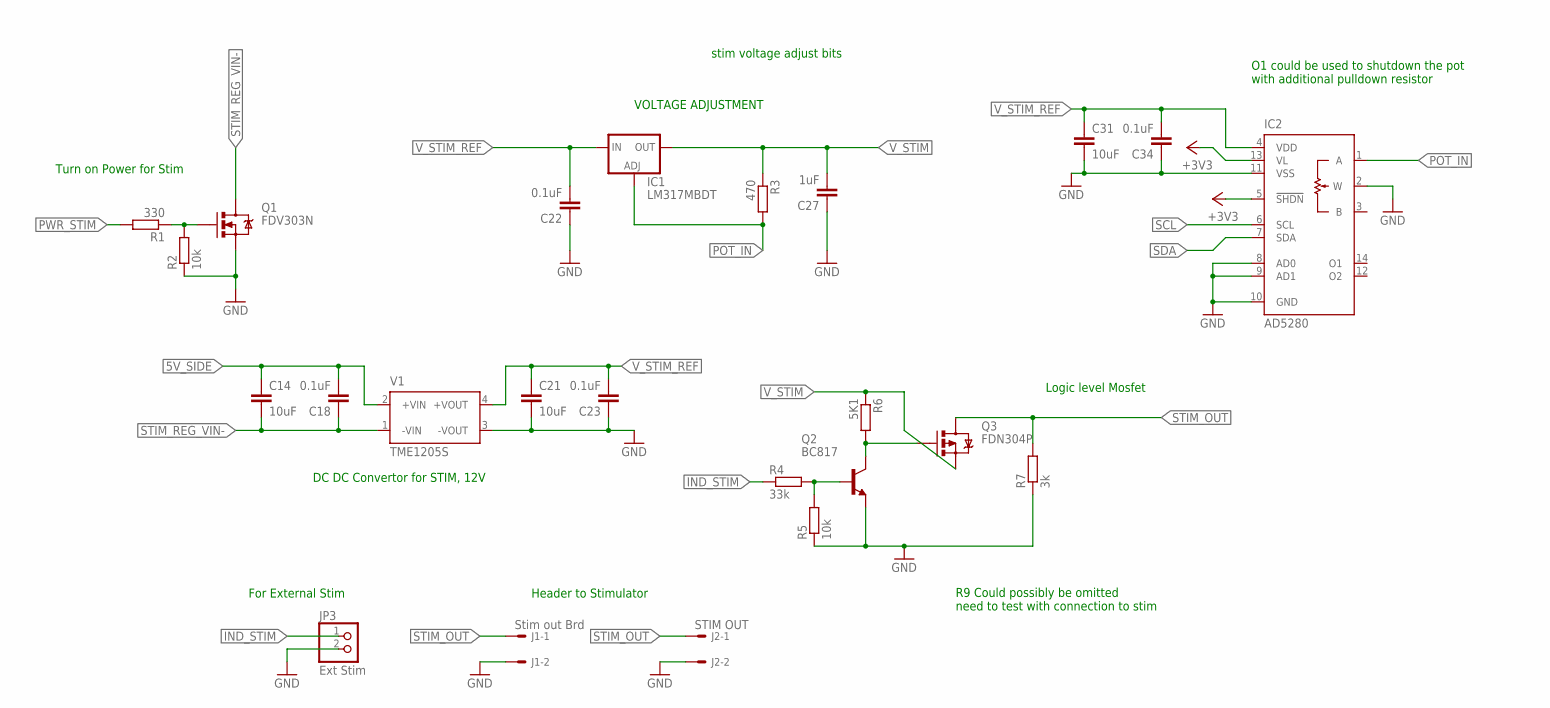
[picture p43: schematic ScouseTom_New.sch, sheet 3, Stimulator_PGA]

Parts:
C14, C21, C31: 10uF; C0805
C18, C22, C23, C34: 0.1uF; C0805
C27: 1uF; C0805
IC1: LM317MBDT; DPACK
IC2: AD5280; TSSOP14
J1: Stim out Brd; 6410-02
J2: STIM OUT; 7395-02
JP3: Ext Stim; 1X02
Q1: FDV303N; SOT323
Q2: BC817; SOT23-BEC
Q3: FDN304P; SOT23-3
R1: 330; R0805
R2, R5: 10k; R0805
R3: 470; R0805
R4: 33k; R0805
R6: 5K1; R0805
R7: 3k; R0805
V1: TME1205S; TME

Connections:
5V_SIDE: C14.1, C18.2, V1.2 (+VIN); also elsewhere on the board
+3V3: IC2.5 (!SHDN), IC2.13 (VL); also elsewhere on the board
GND: C21.2, C22.1, C23.1, C27.1, C31.2, C34.1, IC2.2 (W), IC2.8 (AD0), IC2.9 (AD1), IC2.10 (GND), IC2.11 (VSS), J1.2, J2.2, JP3.2, Q1.2 (S), Q2.E, R2.1, R5.1, R7.1, V1.3 (-VOUT); also elsewhere on the board
IND_STIM: JP3.1, R4.1; also elsewhere on the board
unnamed: Q2.B, R4.2, R5.2
unnamed: Q2.C, Q3.1 (G), R6.2
unnamed: Q1.1 (G), R1.1, R2.2
POT_IN: IC1.1 (ADJ), IC2.1 (A), R3.2
PWR_STIM: R1.2; also elsewhere on the board
SCL: IC2.6 (SCL); also elsewhere on the board
SDA: IC2.7 (SDA); also elsewhere on the board
STIM_OUT: J1.1, J2.1, Q3.3 (D), R7.2
STIM_REG_VIN-: C14.2, C18.1, Q1.3 (D), V1.1 (-VIN)
V_STIM: C27.2, IC1.4 (OUT), Q3.2 (S), R3.1, R6.1
V_STIM_REF: C21.1, C22.2, C23.2, C31.1, C34.2, IC1.3 (IN), IC2.4 (VDD), V1.4 (+VOUT)

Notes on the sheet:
stim voltage adjust bits
Header to Stimulator
Logic level Mosfet
For External Stim
R9 Could possibly be omitted need to test with connection to stim
O1 could be used to shutdown the pot with additional pulldown resistor
Turn on Power for Stim
DC DC Convertor for STIM, 12V
VOLTAGE ADJUSTMENT

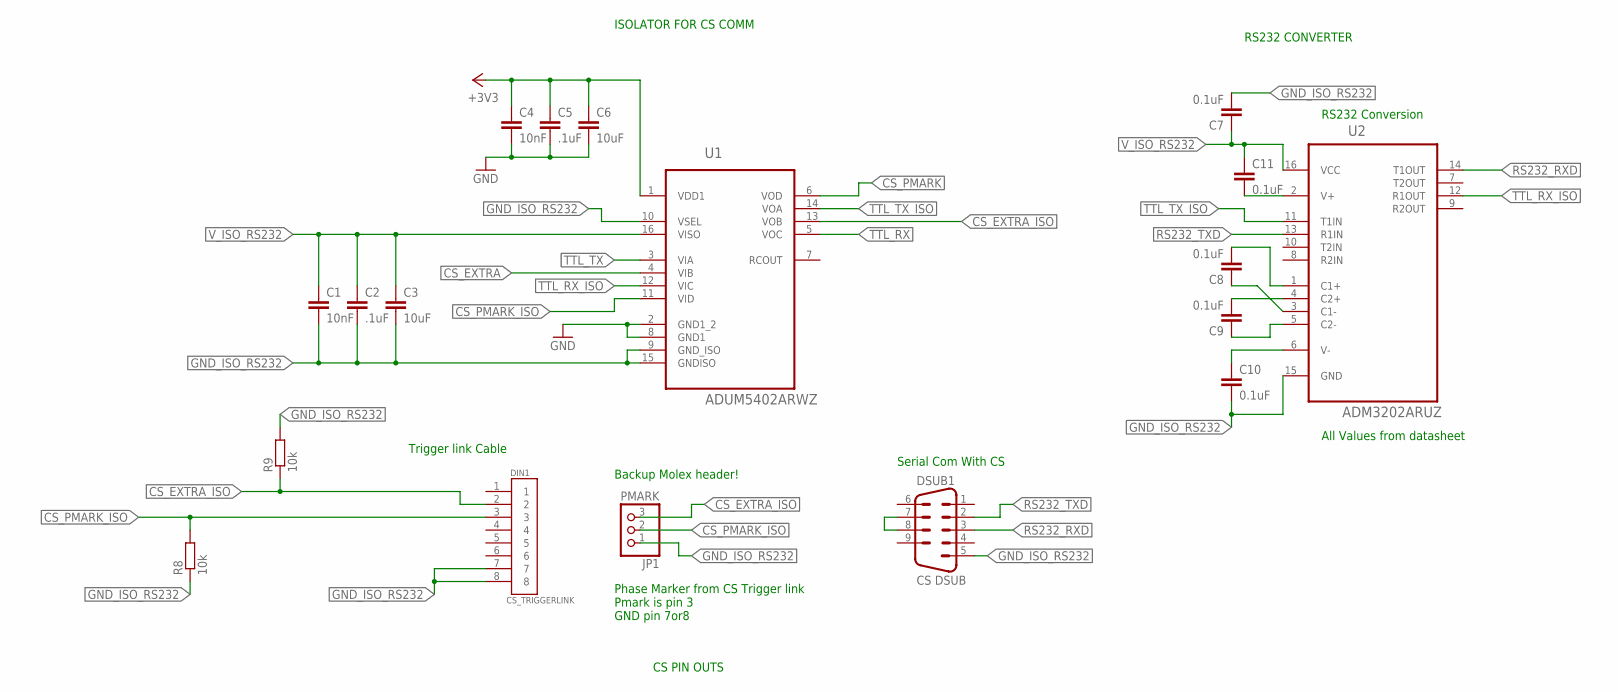
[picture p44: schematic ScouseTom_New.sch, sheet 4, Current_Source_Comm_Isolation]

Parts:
C1, C4: 10nF; C0805
C2, C5: .1uF; C0805
C3, C6: 10uF; C0805
C7, C8, C9, C10, C11: 0.1uF; C0805
DIN1: CS_TRIGGERLINK; DIN8
DSUB1: CS DSUB; DSUB9
JP1: PMARK; 1X03
R8, R9: 10k; R0805
U1: ADUM5402ARWZ; SOIC127P1032X265-16N
U2: ADM3202ARUZ; SOP65P640X120-16N

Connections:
+3V3: C4.1, C5.1, C6.1, U1.1 (VDD1); also elsewhere on the board
CS_EXTRA: U1.4 (VIB); also elsewhere on the board
CS_EXTRA_ISO: DIN1.2, JP1.3, R9.1, U1.13 (VOB)
CS_PMARK: U1.6 (VOD); also elsewhere on the board
CS_PMARK_ISO: DIN1.3, JP1.2, R8.2, U1.11 (VID)
GND: C4.2, C5.2, C6.2, U1.2 (GND1_2), U1.8 (GND1); also elsewhere on the board
GND_ISO_RS232: C1.2, C2.2, C3.2, C7.2, C10.2, DIN1.7, DIN1.8, DSUB1.5, JP1.1, R8.1, R9.2, U1.9 (GND_ISO), U1.10 (VSEL), U1.15 (GNDISO), U2.15 (GND)
unnamed: DSUB1.7, DSUB1.8
unnamed: C8.2, U2.1 (C1+)
unnamed: C8.1, U2.3 (C1-)
unnamed: C9.2, U2.4 (C2+)
unnamed: C9.1, U2.5 (C2-)
unnamed: C11.2, U2.2 (V+)
unnamed: C10.1, U2.6 (V-)
RS232_RXD: DSUB1.3, U2.14 (T1OUT)
RS232_TXD: DSUB1.2, U2.13 (R1IN)
TTL_RX: U1.5 (VOC); also elsewhere on the board
TTL_RX_ISO: U1.12 (VIC), U2.12 (R1OUT)
TTL_TX: U1.3 (VIA); also elsewhere on the board
TTL_TX_ISO: U1.14 (VOA), U2.11 (T1IN)
V_ISO_RS232: C1.1, C2.1, C3.1, C7.1, C11.1, U1.16 (VISO), U2.16 (VCC)

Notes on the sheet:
RS232 Conversion
Phase Marker from CS Trigger link Pmark is pin 3 GND pin 7or8
Backup Molex header!
ISOLATOR FOR CS COMM
RS232 CONVERTER
CS PIN OUTS
Trigger link Cable
Serial Com With CS
All Values from datasheet

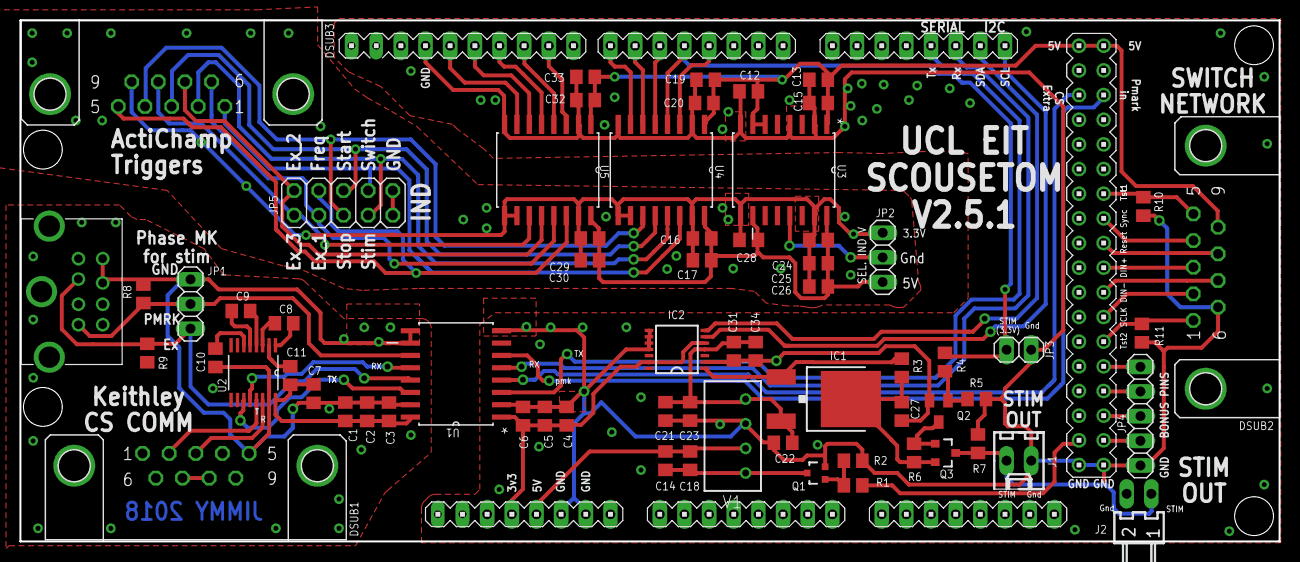
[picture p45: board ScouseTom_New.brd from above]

Board: 2 copper layers, 129.7 x 53.7 mm, 68 parts (0 on the bottom side), 66 nets.

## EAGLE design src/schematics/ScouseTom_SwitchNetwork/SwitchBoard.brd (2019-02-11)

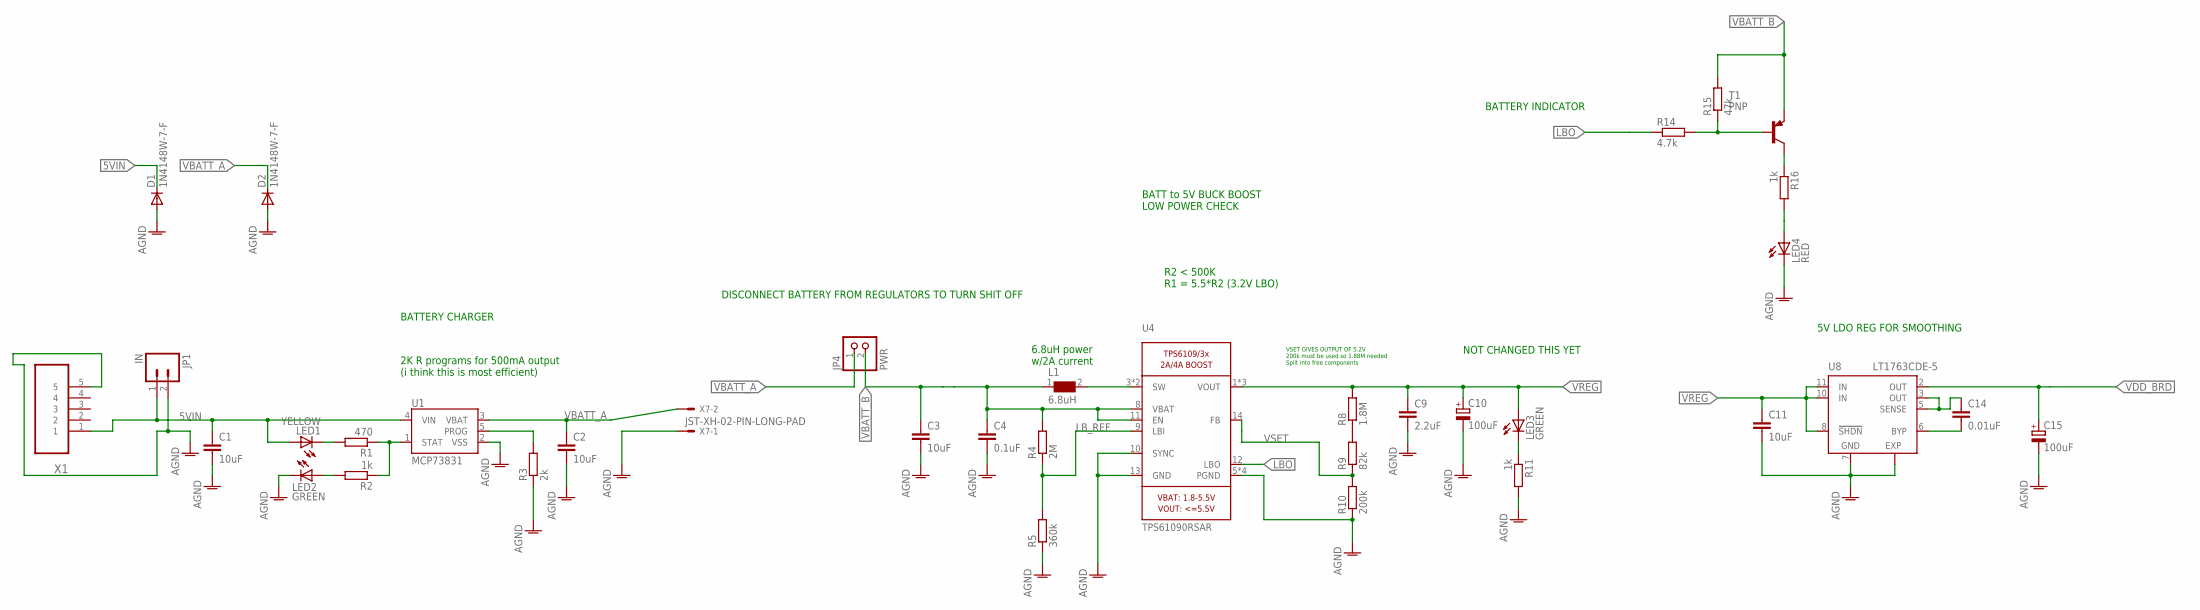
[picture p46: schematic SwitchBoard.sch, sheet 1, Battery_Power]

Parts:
C1, C2, C3, C11: 10uF; C0805
C4: 0.1uF; C0805
C9: 2.2uF; C0805
C10, C15: 100uF; CT6032
C14: 0.01uF; C0805
D1, D2: 1N4148W-7-F; SOD123
JP1: IN; 1X02
JP4: PWR; 1X02
L1: 6.8uH; WE-PD_7332/7345_PLASTIC_BASE
LED1: YELLOW; SML0805
LED2, LED3: GREEN; SML0805
LED4: RED; SML0805
R1: 470; M0805
R2, R11, R16: 1k; M0805
R3: 2k; M0805
R4: 2M; M0805
R5: 360k; M0805
R8: 1.8M; M0805
R9: 82k; M0805
R10: 200k; M0805
R14: 4.7k; M0805
R15: 47k; M0805
T1: PNP; SOT23-BEC
U1: MCP73831; SOT23-5
U4: TPS61090RSAR; QFN16-4X4
U8: LT1763CDE-5; DFN12
X1: 47346-0001; MOLEX_47346-0001
X7: JST-XH-02-PIN-LONG-PAD; JST-XH-02-PACKAGE-LONG-PAD

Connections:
5VIN: C1.1, D1.C, JP1.1, LED1.A, U1.4 (VIN), X1.1
AGND: C1.2, C2.2, C3.2, C4.2, C9.2, C10.-, C11.2, C15.-, D1.A, D2.A, JP1.2, LED2.C, LED4.C, R3.1, R5.1, R10.1, R11.2, U1.2 (VSS), U4.5 (PGND), U4.6 (PGND), U4.7 (PGND), U4.10 (SYNC), U4.13 (GND), U4.EXP (PGND), U8.7 (GND), U8.EXP, X1.5, X7.1; also elsewhere on the board
CHRG: LED1.C, R1.2
LBO: R14.1, U4.12 (LBO)
LB_REF: R4.1, R5.2, U4.9 (LBI)
unnamed: C14.1, U8.3 (OUT), U8.5 (SENSE)
unnamed: C14.2, U8.6 (BYP)
unnamed: LED2.A, R2.2
unnamed: R8.1, R9.2
unnamed: LED3.C, R11.1
unnamed: R16.1, T1.C
unnamed: LED4.A, R16.2
unnamed: R14.2, R15.1, T1.B
PROG: R3.2, U1.5 (PROG)
STAT: R1.1, R2.1, U1.1 (STAT)
SW: L1.2, U4.3 (SW), U4.4 (SW)
VBATT_A: C2.1, D2.C, JP4.1, U1.3 (VBAT), X7.2
VBATT_B: C3.1, C4.1, JP4.2, L1.1, R4.2, R15.2, T1.E, U4.8 (VBAT), U4.11 (EN)
VDD_BRD: C15.+, U8.2 (OUT); also elsewhere on the board
VREG: C9.1, C10.+, C11.1, LED3.A, R8.2, U4.1 (VOUT), U4.15 (VOUT), U4.16 (VOUT), U8.8 (!SHDN), U8.10 (IN), U8.11 (IN)
VSET: R9.1, R10.2, U4.14 (FB)

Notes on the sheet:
BATTERY CHARGER
BATT to 5V BUCK BOOST LOW POWER CHECK
5V LDO REG FOR SMOOTHING
6.8uH power w/2A current
R2 < 500K R1 = 5.5*R2 (3.2V LBO)
BATTERY INDICATOR
VSET GIVES OUTPUT OF 5.2V 200k must be used so 1.88M needed Split into free components
NOT CHANGED THIS YET
2K R programs for 500mA output (i think this is most efficient)
DISCONNECT BATTERY FROM REGULATORS TO TURN SHIT OFF

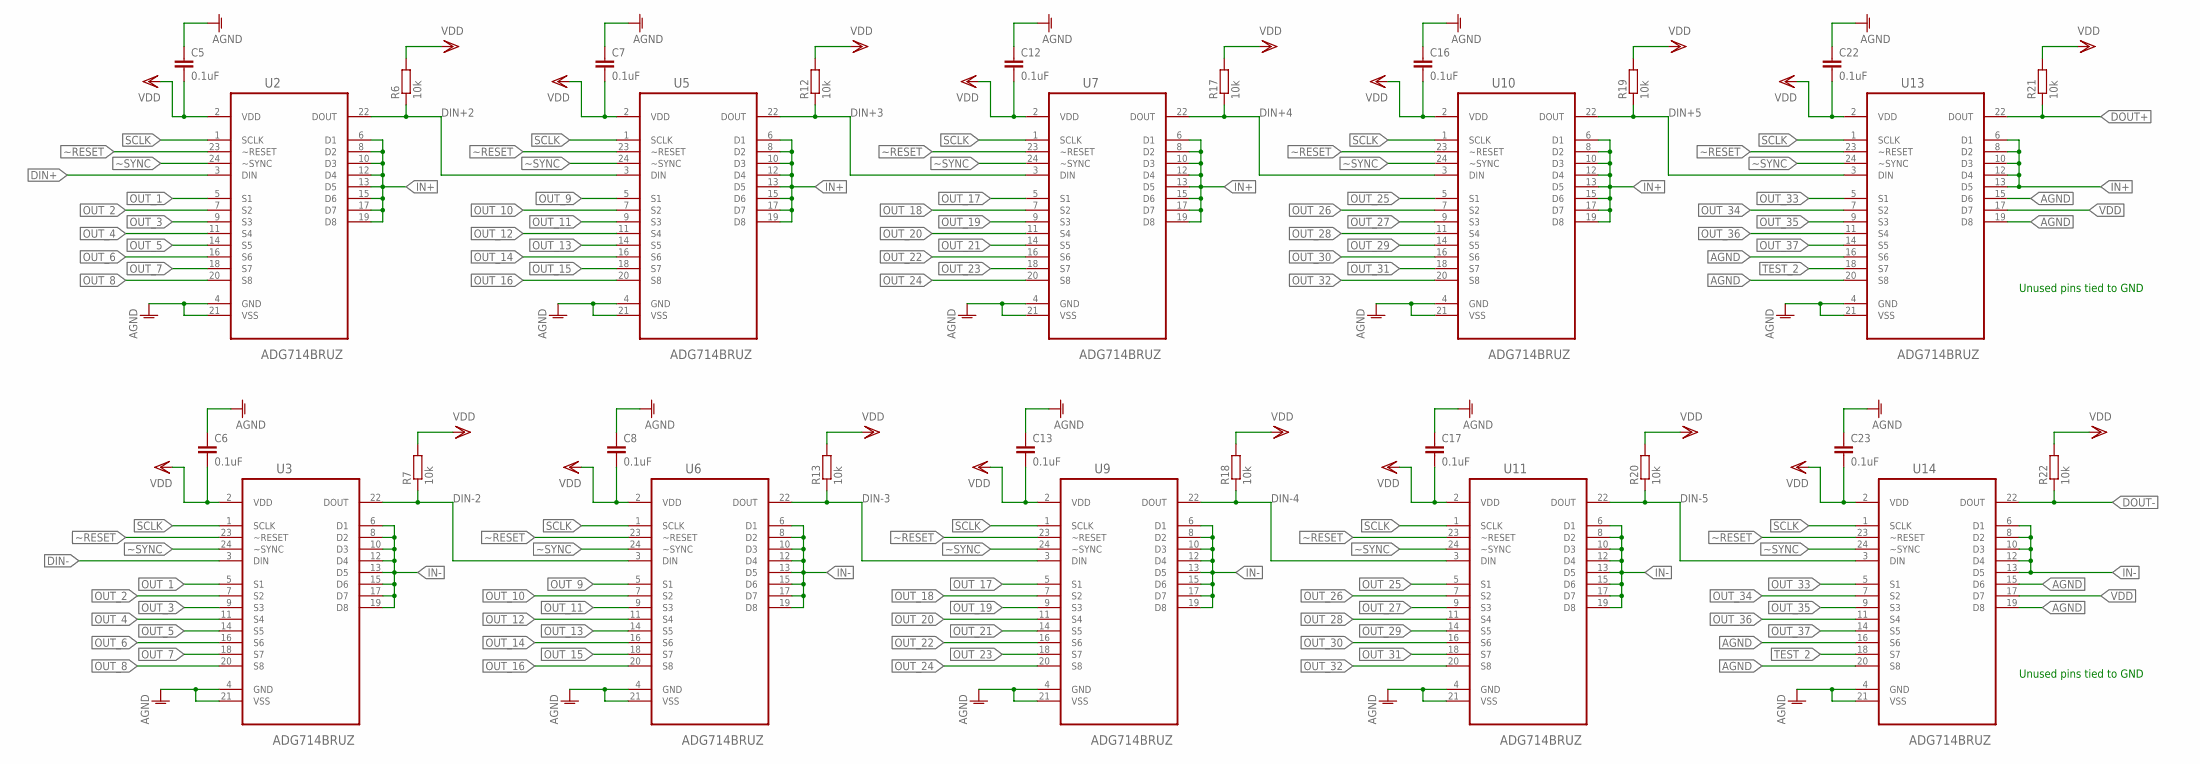
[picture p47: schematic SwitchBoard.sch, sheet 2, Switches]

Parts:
C5, C6, C7, C8, C12, C13, C16, C17, C22, C23: 0.1uF; C0805
R6, R7, R12, R13, R17, R18, R19, R20, R21, R22: 10k; M0805
U2, U3, U5, U6, U7, U9, U10, U11, U13, U14: ADG714BRUZ; SOP65P640X120-24N

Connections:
AGND: C5.1, C6.1, C7.1, C8.1, C12.1, C13.1, C16.1, C17.1, C22.1, C23.1, U2.4 (GND), U2.21 (VSS), U3.4 (GND), U3.21 (VSS), U5.4 (GND), U5.21 (VSS), U6.4 (GND), U6.21 (VSS), U7.4 (GND), U7.21 (VSS), U9.4 (GND), U9.21 (VSS), U10.4 (GND), U10.21 (VSS), U11.4 (GND), U11.21 (VSS), U13.4 (GND), U13.15 (D6), U13.16 (S6), U13.19 (D8), U13.20 (S8), U13.21 (VSS), U14.4 (GND), U14.15 (D6), U14.16 (S6), U14.19 (D8), U14.20 (S8), U14.21 (VSS); also elsewhere on the board
DIN+: U2.3 (DIN); also elsewhere on the board
DIN+2: R6.1, U2.22 (DOUT), U5.3 (DIN)
DIN+3: R12.1, U5.22 (DOUT), U7.3 (DIN)
DIN+4: R17.1, U7.22 (DOUT), U10.3 (DIN)
DIN+5: R19.1, U10.22 (DOUT), U13.3 (DIN)
DIN-: U3.3 (DIN); also elsewhere on the board
DIN-2: R7.1, U3.22 (DOUT), U6.3 (DIN)
DIN-3: R13.1, U6.22 (DOUT), U9.3 (DIN)
DIN-4: R18.1, U9.22 (DOUT), U11.3 (DIN)
DIN-5: R20.1, U11.22 (DOUT), U14.3 (DIN)
DOUT+: R21.1, U13.22 (DOUT); also elsewhere on the board
DOUT-: R22.1, U14.22 (DOUT); also elsewhere on the board
IN+: U2.6 (D1), U2.8 (D2), U2.10 (D3), U2.12 (D4), U2.13 (D5), U2.15 (D6), U2.17 (D7), U2.19 (D8), U5.6 (D1), U5.8 (D2), U5.10 (D3), U5.12 (D4), U5.13 (D5), U5.15 (D6), U5.17 (D7), U5.19 (D8), U7.6 (D1), U7.8 (D2), U7.10 (D3), U7.12 (D4), U7.13 (D5), U7.15 (D6), U7.17 (D7), U7.19 (D8), U10.6 (D1), U10.8 (D2), U10.10 (D3), U10.12 (D4), U10.13 (D5), U10.15 (D6), U10.17 (D7), U10.19 (D8), U13.6 (D1), U13.8 (D2), U13.10 (D3), U13.12 (D4), U13.13 (D5); also elsewhere on the board
IN-: U3.6 (D1), U3.8 (D2), U3.10 (D3), U3.12 (D4), U3.13 (D5), U3.15 (D6), U3.17 (D7), U3.19 (D8), U6.6 (D1), U6.8 (D2), U6.10 (D3), U6.12 (D4), U6.13 (D5), U6.15 (D6), U6.17 (D7), U6.19 (D8), U9.6 (D1), U9.8 (D2), U9.10 (D3), U9.12 (D4), U9.13 (D5), U9.15 (D6), U9.17 (D7), U9.19 (D8), U11.6 (D1), U11.8 (D2), U11.10 (D3), U11.12 (D4), U11.13 (D5), U11.15 (D6), U11.17 (D7), U11.19 (D8), U14.6 (D1), U14.8 (D2), U14.10 (D3), U14.12 (D4), U14.13 (D5); also elsewhere on the board
OUT_1: U2.5 (S1), U3.5 (S1); also elsewhere on the board
OUT_2: U2.7 (S2), U3.7 (S2); also elsewhere on the board
OUT_3: U2.9 (S3), U3.9 (S3); also elsewhere on the board
OUT_4: U2.11 (S4), U3.11 (S4); also elsewhere on the board
OUT_5: U2.14 (S5), U3.14 (S5); also elsewhere on the board
OUT_6: U2.16 (S6), U3.16 (S6); also elsewhere on the board
OUT_7: U2.18 (S7), U3.18 (S7); also elsewhere on the board
OUT_8: U2.20 (S8), U3.20 (S8); also elsewhere on the board
OUT_9: U5.5 (S1), U6.5 (S1); also elsewhere on the board
OUT_10: U5.7 (S2), U6.7 (S2); also elsewhere on the board
OUT_11: U5.9 (S3), U6.9 (S3); also elsewhere on the board
OUT_12: U5.11 (S4), U6.11 (S4); also elsewhere on the board
OUT_13: U5.14 (S5), U6.14 (S5); also elsewhere on the board
OUT_14: U5.16 (S6), U6.16 (S6); also elsewhere on the board
OUT_15: U5.18 (S7), U6.18 (S7); also elsewhere on the board
OUT_16: U5.20 (S8), U6.20 (S8); also elsewhere on the board
OUT_17: U7.5 (S1), U9.5 (S1); also elsewhere on the board
OUT_18: U7.7 (S2), U9.7 (S2); also elsewhere on the board
OUT_19: U7.9 (S3), U9.9 (S3); also elsewhere on the board
OUT_20: U7.11 (S4), U9.11 (S4); also elsewhere on the board
OUT_21: U7.14 (S5), U9.14 (S5); also elsewhere on the board
OUT_22: U7.16 (S6), U9.16 (S6); also elsewhere on the board
OUT_23: U7.18 (S7), U9.18 (S7); also elsewhere on the board
OUT_24: U7.20 (S8), U9.20 (S8); also elsewhere on the board
OUT_25: U10.5 (S1), U11.5 (S1); also elsewhere on the board
OUT_26: U10.7 (S2), U11.7 (S2); also elsewhere on the board
OUT_27: U10.9 (S3), U11.9 (S3); also elsewhere on the board
OUT_28: U10.11 (S4), U11.11 (S4); also elsewhere on the board
OUT_29: U10.14 (S5), U11.14 (S5); also elsewhere on the board
OUT_30: U10.16 (S6), U11.16 (S6); also elsewhere on the board
OUT_31: U10.18 (S7), U11.18 (S7); also elsewhere on the board
OUT_32: U10.20 (S8), U11.20 (S8); also elsewhere on the board
OUT_33: U13.5 (S1), U14.5 (S1); also elsewhere on the board
OUT_34: U13.7 (S2), U14.7 (S2); also elsewhere on the board
OUT_35: U13.9 (S3), U14.9 (S3); also elsewhere on the board
OUT_36: U13.11 (S4), U14.11 (S4); also elsewhere on the board
OUT_37: U13.14 (S5), U14.14 (S5); also elsewhere on the board
SCLK: U2.1 (SCLK), U3.1 (SCLK), U5.1 (SCLK), U6.1 (SCLK), U7.1 (SCLK), U9.1 (SCLK), U10.1 (SCLK), U11.1 (SCLK), U13.1 (SCLK), U14.1 (SCLK); also elsewhere on the board
TEST_2: U13.18 (S7), U14.18 (S7); also elsewhere on the board
VDD: C5.2, C6.2, C7.2, C8.2, C12.2, C13.2, C16.2, C17.2, C22.2, C23.2, R6.2, R7.2, R12.2, R13.2, R17.2, R18.2, R19.2, R20.2, R21.2, R22.2, U2.2 (VDD), U3.2 (VDD), U5.2 (VDD), U6.2 (VDD), U7.2 (VDD), U9.2 (VDD), U10.2 (VDD), U11.2 (VDD), U13.2 (VDD), U13.17 (D7), U14.2 (VDD), U14.17 (D7); also elsewhere on the board
~RESET: U2.23 (~RESET), U3.23 (~RESET), U5.23 (~RESET), U6.23 (~RESET), U7.23 (~RESET), U9.23 (~RESET), U10.23 (~RESET), U11.23 (~RESET), U13.23 (~RESET), U14.23 (~RESET); also elsewhere on the board
~SYNC: U2.24 (~SYNC), U3.24 (~SYNC), U5.24 (~SYNC), U6.24 (~SYNC), U7.24 (~SYNC), U9.24 (~SYNC), U10.24 (~SYNC), U11.24 (~SYNC), U13.24 (~SYNC), U14.24 (~SYNC); also elsewhere on the board

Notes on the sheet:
Unused pins tied to GND

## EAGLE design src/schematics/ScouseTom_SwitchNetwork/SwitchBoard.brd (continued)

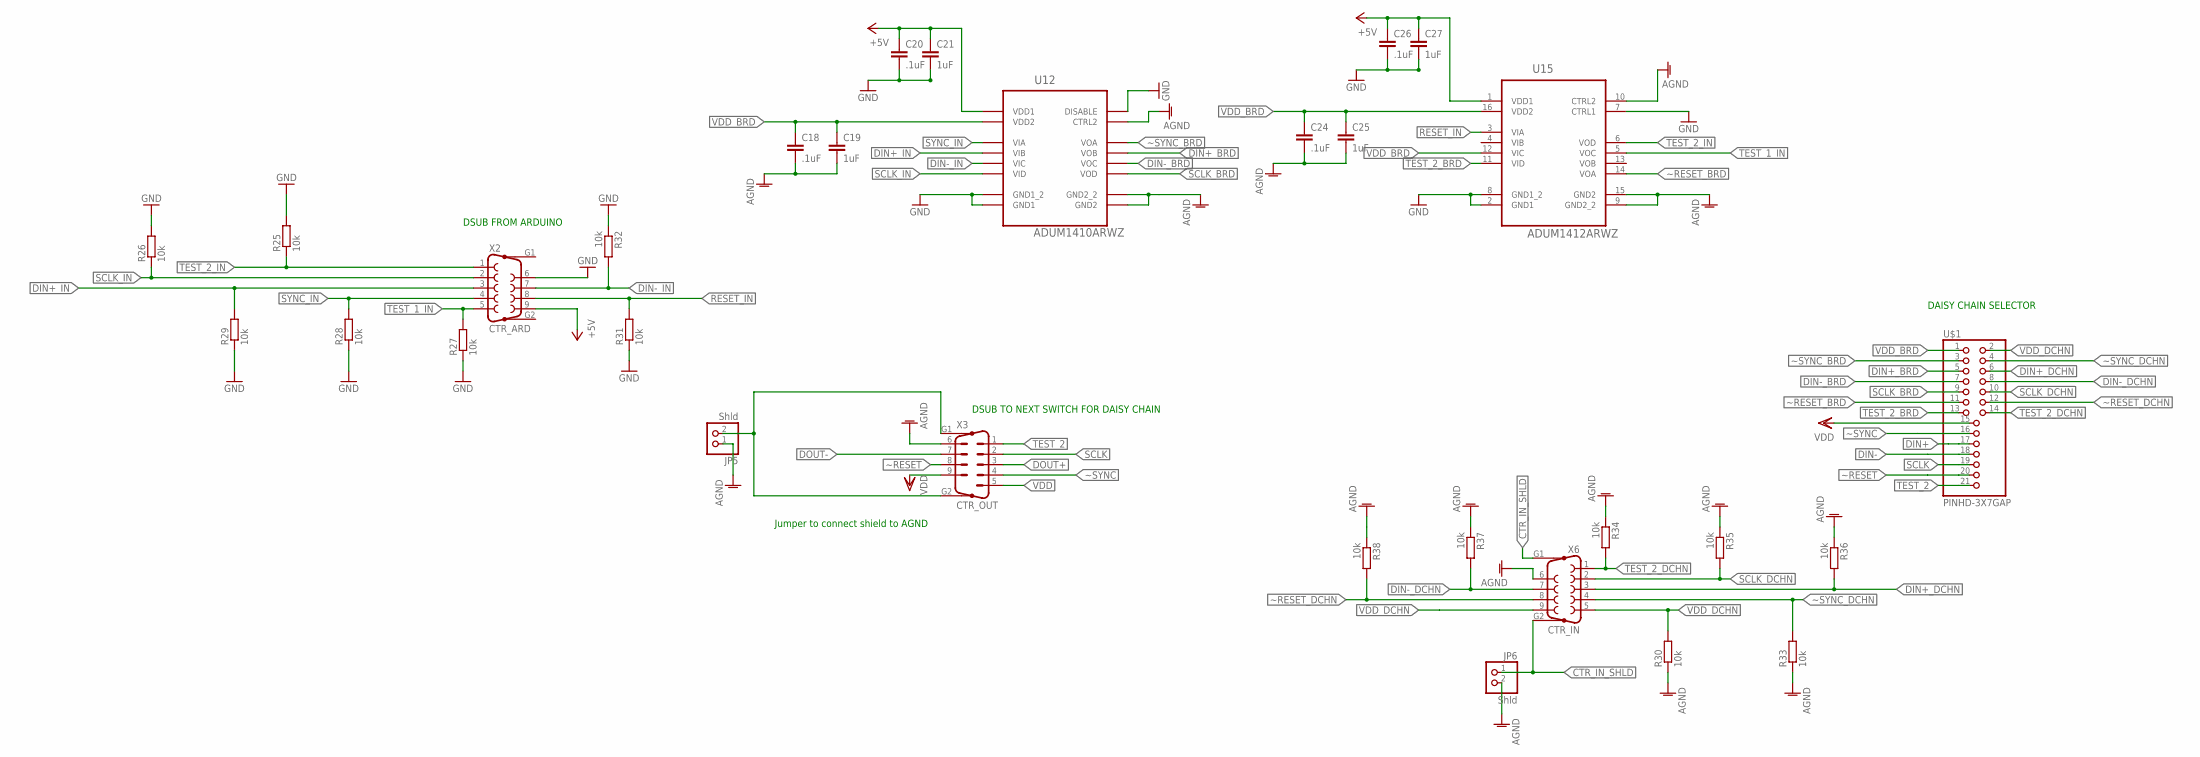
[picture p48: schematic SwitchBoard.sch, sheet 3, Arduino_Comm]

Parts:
C18, C20, C24, C26: .1uF; C0805
C19, C21, C25, C27: 1uF; C0805
JP5, JP6: Shld; 1X02
R25, R26, R27, R28, R29, R30, R31, R32, R33, R34, R35, R36, R37, R38: 10k; R0402
U12: ADUM1410ARWZ; SOIC127P1032X265-16N
U15: ADUM1412ARWZ; SOIC127P1032X265-16N
U$1: PINHD-3X7GAP; 3X07
X2: CTR_ARD; F09HP
X3: CTR_OUT; M09HP
X6: CTR_IN; F09HP

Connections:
+5V: C20.1, C21.1, C26.1, C27.1, U12.1 (VDD1), U15.1 (VDD1), X2.9
AGND: C18.2, C19.2, C24.2, C25.2, JP5.1, JP6.2, R30.1, R33.1, R34.1, R35.1, R36.1, R37.1, R38.1, U12.9 (GND2_2), U12.10 (CTRL2), U12.15 (GND2), U15.9 (GND2_2), U15.10 (CTRL2), U15.15 (GND2), X3.6, X6.6; also elsewhere on the board
CTR_IN_SHLD: JP6.1, X6.G1, X6.G2
DIN+: U$1.17; also elsewhere on the board
DIN+_BRD: U12.13 (VOB), U$1.5
DIN+_DCHN: R36.2, U$1.6, X6.3
DIN+_IN: R29.2, U12.4 (VIB), X2.3
DIN-: U$1.18; also elsewhere on the board
DIN-_BRD: U12.12 (VOC), U$1.7
DIN-_DCHN: R37.2, U$1.8, X6.7
DIN-_IN: R32.2, U12.5 (VIC), X2.7
DOUT+: X3.3; also elsewhere on the board
DOUT-: X3.7; also elsewhere on the board
GND: C20.2, C21.2, C26.2, C27.2, R25.2, R26.2, R27.1, R28.1, R29.1, R31.1, R32.1, U12.2 (GND1_2), U12.7 (DISABLE), U12.8 (GND1), U15.2 (GND1), U15.7 (CTRL1), U15.8 (GND1_2), X2.6
unnamed: JP5.2, X3.G1, X3.G2
RESET_IN: R31.2, U15.3 (VIA), X2.8
SCLK: U$1.19, X3.2; also elsewhere on the board
SCLK_BRD: U12.11 (VOD), U$1.9
SCLK_DCHN: R35.2, U$1.10, X6.2
SCLK_IN: R26.1, U12.6 (VID), X2.2
SYNC_IN: R28.2, U12.3 (VIA), X2.4
TEST_1_IN: R27.2, U15.5 (VOC), X2.5
TEST_2: U$1.21, X3.1; also elsewhere on the board
TEST_2_BRD: U15.11 (VID), U$1.13
TEST_2_DCHN: R34.2, U$1.14, X6.1
TEST_2_IN: R25.1, U15.6 (VOD), X2.1
VDD: U$1.15, X3.5, X3.9; also elsewhere on the board
VDD_BRD: C18.1, C19.1, C24.1, C25.1, U12.16 (VDD2), U15.12 (VIC), U15.16 (VDD2), U$1.1; also elsewhere on the board
VDD_DCHN: R30.2, U$1.2, X6.5, X6.9
~RESET: U$1.20, X3.8; also elsewhere on the board
~RESET_BRD: U15.14 (VOA), U$1.11
~RESET_DCHN: R38.2, U$1.12, X6.8
~SYNC: U$1.16, X3.4; also elsewhere on the board
~SYNC_BRD: U12.14 (VOA), U$1.3
~SYNC_DCHN: R33.2, U$1.4, X6.4

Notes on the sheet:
DSUB FROM ARDUINO
Jumper to connect shield to AGND
DSUB TO NEXT SWITCH FOR DAISY CHAIN
DAISY CHAIN SELECTOR

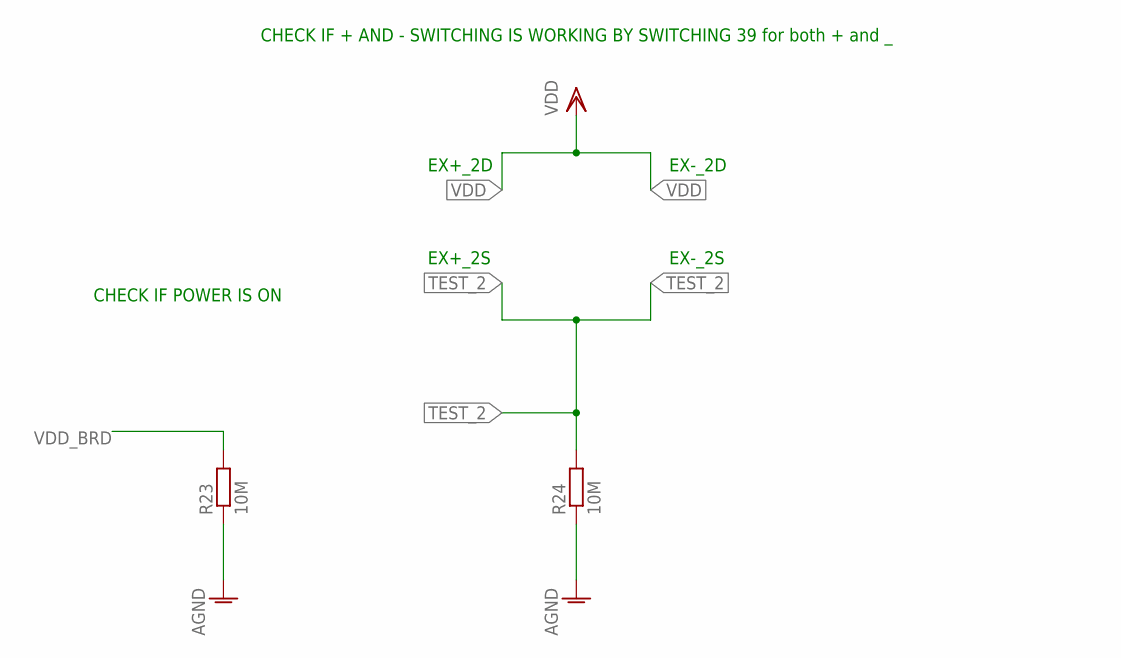
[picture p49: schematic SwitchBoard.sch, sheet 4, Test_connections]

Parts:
R23, R24: 10M; M0805

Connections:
AGND: R23.1, R24.1; also elsewhere on the board
TEST_2: R24.2; also elsewhere on the board
VDD_BRD: R23.2; also elsewhere on the board

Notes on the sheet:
EX+_2D
EX-_2D
EX-_2S
EX+_2S
CHECK IF POWER IS ON
CHECK IF + AND - SWITCHING IS WORKING BY SWITCHING 39 for both + and _

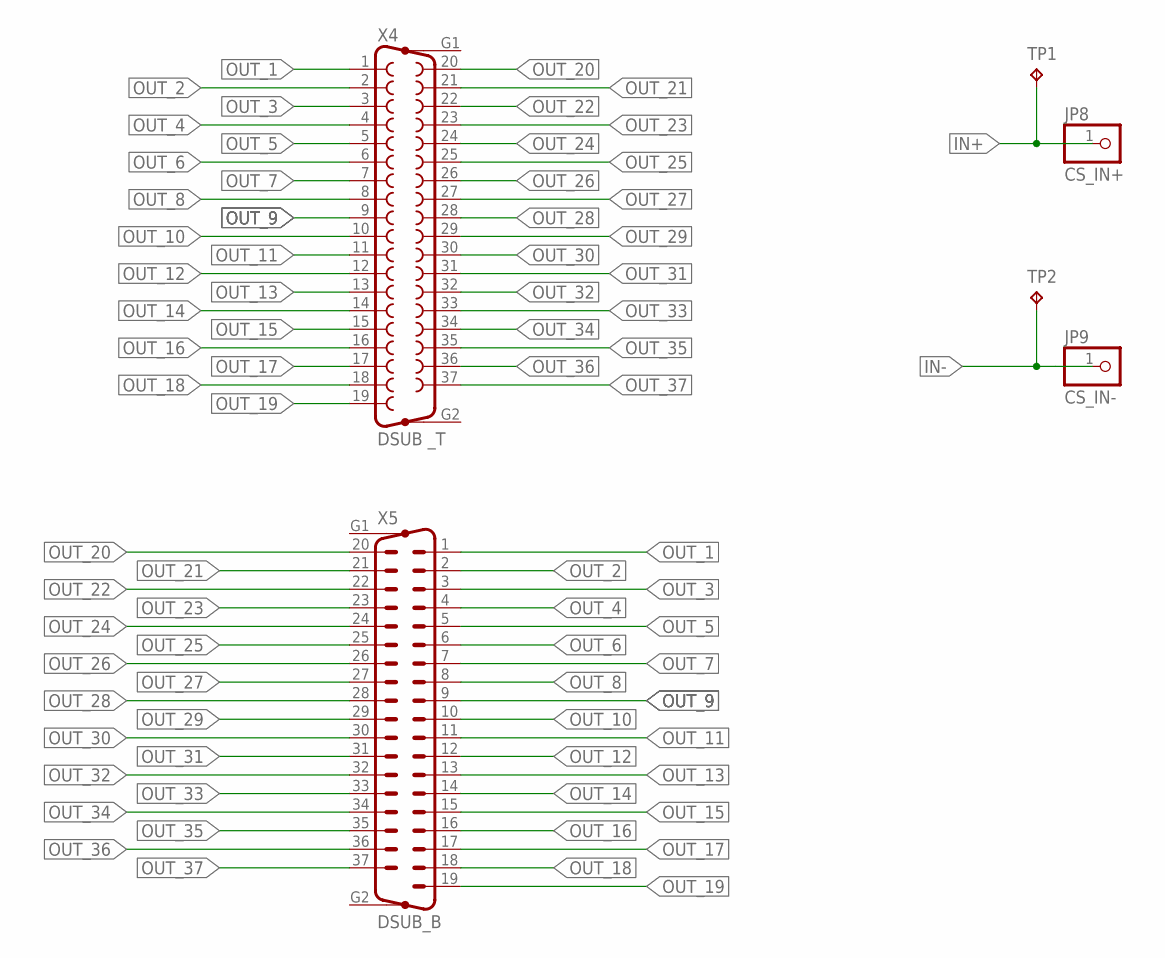
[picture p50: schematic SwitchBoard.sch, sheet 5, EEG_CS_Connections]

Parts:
JP8: CS_IN+; 1X01
JP9: CS_IN-; 1X01
TP1, TP2: TPPAD1-20; P1-20
X4: DSUB _T; F37HP
X5: DSUB_B; M37HP

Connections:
IN+: JP8.1, TP1.TP; also elsewhere on the board
IN-: JP9.1, TP2.TP; also elsewhere on the board
OUT_1: X4.1, X5.1; also elsewhere on the board
OUT_2: X4.2, X5.2; also elsewhere on the board
OUT_3: X4.3, X5.3; also elsewhere on the board
OUT_4: X4.4, X5.4; also elsewhere on the board
OUT_5: X4.5, X5.5; also elsewhere on the board
OUT_6: X4.6, X5.6; also elsewhere on the board
OUT_7: X4.7, X5.7; also elsewhere on the board
OUT_8: X4.8, X5.8; also elsewhere on the board
OUT_9: X4.9, X5.9; also elsewhere on the board
OUT_10: X4.10, X5.10; also elsewhere on the board
OUT_11: X4.11, X5.11; also elsewhere on the board
OUT_12: X4.12, X5.12; also elsewhere on the board
OUT_13: X4.13, X5.13; also elsewhere on the board
OUT_14: X4.14, X5.14; also elsewhere on the board
OUT_15: X4.15, X5.15; also elsewhere on the board
OUT_16: X4.16, X5.16; also elsewhere on the board
OUT_17: X4.17, X5.17; also elsewhere on the board
OUT_18: X4.18, X5.18; also elsewhere on the board
OUT_19: X4.19, X5.19; also elsewhere on the board
OUT_20: X4.20, X5.20; also elsewhere on the board
OUT_21: X4.21, X5.21; also elsewhere on the board
OUT_22: X4.22, X5.22; also elsewhere on the board
OUT_23: X4.23, X5.23; also elsewhere on the board
OUT_24: X4.24, X5.24; also elsewhere on the board
OUT_25: X4.25, X5.25; also elsewhere on the board
OUT_26: X4.26, X5.26; also elsewhere on the board
OUT_27: X4.27, X5.27; also elsewhere on the board
OUT_28: X4.28, X5.28; also elsewhere on the board
OUT_29: X4.29, X5.29; also elsewhere on the board
OUT_30: X4.30, X5.30; also elsewhere on the board
OUT_31: X4.31, X5.31; also elsewhere on the board
OUT_32: X4.32, X5.32; also elsewhere on the board
OUT_33: X4.33, X5.33; also elsewhere on the board
OUT_34: X4.34, X5.34; also elsewhere on the board
OUT_35: X4.35, X5.35; also elsewhere on the board
OUT_36: X4.36, X5.36; also elsewhere on the board
OUT_37: X4.37, X5.37; also elsewhere on the board



Board: 2 copper layers, 169.5 x 97.5 mm, 104 parts (19 on the bottom side), 101 nets.

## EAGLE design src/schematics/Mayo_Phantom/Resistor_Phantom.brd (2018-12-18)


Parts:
J1: 22-27-2041-04; 6410-04
JP1: GNDHDR; 1X01
K1, K2, K3: AQY22SOP; SOP04
R1, R2, R3, R4, R5, R6, R7, R8, R9, R10, R11, R12, R13, R14, R15, R16, R17, R18, R19, R20, R21, R22, R23, R24, R25, R26, R27, R28, R29, R30, R31, R32, R33, R34, R35, R36, R37, R38, R39, R40, R41, R42, R43, R44, R45, R46, R47, R48, R49, R50, R51, R52, R53, R54, R55, R56, R57, R58, R59, R60, R61, R62, R63, R64, R129, R130, R131, R132, R133, R134, R135, R136, R137, R138, R139, R140, R141, R142, R143, R144, R145, R146, R147, R148, R149, R150, R151, R152, R153, R154, R155, R156, R157, R158, R159, R160: 1k; R0402
R65, R66, R67, R68, R69, R70, R71, R72, R73, R74, R75, R76, R77, R78, R79, R80, R81, R82, R83, R84, R85, R86, R87, R88, R89, R90, R91, R92, R93, R94, R95, R96: 3k; R0402
R97, R98, R99, R100, R101, R102, R103, R104, R105, R106, R107, R108, R109, R110, R111, R112, R113, R114, R115, R116, R117, R118, R119, R120, R121, R122, R123, R124, R125, R126, R127, R128, R174, R175: 500; R0402
R163, R164, R165, R168, R171: 10k; R0402
R172, R173: 2k; R0402
R176, R177: 100; R0402
R178: 200; R0402
X1: DSUBIN; F37VP

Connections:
ARD_GND: J1.4, K1.2 (K), K2.2 (K), K3.2 (K)
E1: R1.1, X1.1
E2: R2.1, X1.2
E3: R3.1, X1.3
E4: R4.1, X1.4
E5: R5.1, X1.5
E6: R6.1, X1.6
E7: R7.1, X1.7
E8: R8.1, X1.8
E9: R9.1, X1.9
E10: R10.1, X1.10
E11: R11.1, X1.11
E12: R12.1, X1.12
E13: R13.1, X1.13
E14: R14.1, X1.14
E15: R15.1, X1.15
E16: R16.1, X1.16
E17: R17.1, X1.17
E18: R18.1, X1.18
E19: R19.1, X1.19
E20: R20.1, X1.20
E21: R21.1, X1.21
E22: R22.1, X1.22
E23: R23.1, X1.23
E24: R24.1, X1.24
E25: R25.1, X1.25
E26: R26.1, X1.26
E27: R27.1, X1.27
E28: R28.1, X1.28
E29: R29.1, X1.29
E30: R30.1, X1.30
E31: R31.1, X1.31
E32: R32.1, X1.32
E33: X1.33
E34: X1.34
E35: X1.35
E36: X1.36
E37: X1.37
E38: R1.2, R33.1, R64.2, R65.1
E39: R2.2, R33.2, R34.1, R66.1
E40: R3.2, R34.2, R35.1, R67.1
E41: R4.2, R35.2, R36.1, R68.1
E42: R5.2, R36.2, R37.1, R69.1
E43: R6.2, R37.2, R38.1, R70.1
E44: R7.2, R38.2, R39.1, R71.1
E45: R8.2, R39.2, R40.1, R72.1
E46: R9.2, R40.2, R41.1, R73.1
E47: R10.2, R41.2, R42.1, R74.1
E48: R11.2, R42.2, R43.1, R75.1
E49: R12.2, R43.2, R44.1, R76.1
E50: R13.2, R44.2, R45.1, R77.1
E51: R14.2, R45.2, R46.1, R78.1
E52: R15.2, R46.2, R47.1, R79.1
E53: R16.2, R47.2, R48.1, R80.1
E54: R17.2, R48.2, R49.1, R81.1
E55: R18.2, R49.2, R50.1, R82.1
E56: R19.2, R50.2, R51.1, R83.1
E57: R20.2, R51.2, R52.1, R84.1
E58: R21.2, R52.2, R53.1, R85.1
E59: R22.2, R53.2, R54.1, R86.1
E60: R23.2, R54.2, R55.1, R87.1
E61: R24.2, R55.2, R56.1, R88.1
E63: R26.2, R57.2, R58.1, R90.1
E64: R27.2, R58.2, R59.1, R91.1
E65: R28.2, R59.2, R60.1, R92.1
E66: R29.2, R60.2, R61.1, R93.1
E67: R30.2, R61.2, R62.1, R94.1
E68: R31.2, R62.2, R63.1, R95.1
E69: R32.2, R63.2, R64.1, R96.1
GND: JP1.1, R129.2, R130.2, R131.2, R132.2, R133.2, R134.2, R135.2, R136.2, R137.2, R138.2, R139.2, R140.2, R141.2, R142.2, R143.2, R144.2, R145.2, R146.2, R147.2, R148.2, R149.2, R150.2, R151.2, R152.2, R153.2, R154.2, R155.2, R156.2, R157.2, R158.2, R159.2, R160.2, R171.2, R175.1, R178.2, X1.G1, X1.G2
IN1: J1.1, K1.1 (A)
IN2: J1.2, K2.1 (A)
IN3: J1.3, K3.1 (A)
unnamed: R25.2, R56.2, R57.1, R89.1
unnamed: R65.2, R97.1, R128.2, R129.1
unnamed: R66.2, R97.2, R98.1, R130.1
unnamed: R67.2, R98.2, R99.1, R131.1
unnamed: R68.2, R99.2, R100.1, R132.1
unnamed: R69.2, R100.2, R101.1, R133.1
unnamed: R70.2, R101.2, R102.1, R134.1
unnamed: R71.2, R102.2, R103.1, R135.1
unnamed: R72.2, R103.2, R104.1, R136.1
unnamed: R73.2, R104.2, R105.1, R137.1
unnamed: R75.2, R106.2, R107.1, R139.1
unnamed: R76.2, R107.2, R108.1, R140.1
unnamed: R77.2, R108.2, R109.1, R141.1
unnamed: R78.2, R109.2, R110.1, R142.1
unnamed: R79.2, R110.2, R111.1, R143.1
unnamed: R80.2, R111.2, R112.1, R144.1
unnamed: R81.2, R112.2, R113.1, R145.1
unnamed: R82.2, R113.2, R114.1, R146.1
unnamed: R83.2, R114.2, R115.1, R147.1
unnamed: R85.2, R116.2, R117.1, R149.1
unnamed: R86.2, R117.2, R118.1, R150.1
unnamed: R87.2, R118.2, R119.1, R151.1
unnamed: R88.2, R119.2, R120.1, R152.1
unnamed: R89.2, R120.2, R121.1, R153.1
unnamed: R90.2, R121.2, R122.1, R154.1
unnamed: R91.2, R122.2, R123.1, R155.1
unnamed: R92.2, R123.2, R124.1, R156.1
unnamed: R93.2, R124.2, R125.1, R157.1
unnamed: R95.2, R126.2, R127.1, R159.1
unnamed: R96.2, R127.2, R128.1, R160.1
unnamed: R163.2, R164.2
unnamed: R164.1, R165.1
unnamed: R165.2, R168.2
unnamed: R168.1, R171.1
unnamed: R172.2, R173.2
unnamed: R173.1, R174.1
unnamed: R174.2, R175.2
unnamed: R176.2, R177.1
unnamed: R177.2, R178.1
SW_IN1: K1.4 (DS1), R74.2, R105.2, R106.1, R138.1
SW_IN2: K2.4 (DS1), R84.2, R115.2, R116.1, R148.1
SW_IN3: K3.4 (DS1), R94.2, R125.2, R126.1, R158.1
SW_OUT1: K1.3 (DS2), R163.1
SW_OUT2: K2.3 (DS2), R172.1
SW_OUT3: K3.3 (DS2), R176.1



Board: 2 copper layers, 76.0 x 45.0 mm, 178 parts (16 on the bottom side), 113 nets.

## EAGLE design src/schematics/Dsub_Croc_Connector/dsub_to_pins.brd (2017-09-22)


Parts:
PAD1, PAD2, PAD3, PAD4, PAD5, PAD6, PAD7, PAD8, PAD9, PAD10, PAD11, PAD12, PAD13, PAD14, PAD15, PAD16, PAD17, PAD18, PAD19, PAD20, PAD21, PAD22, PAD23, PAD24, PAD25, PAD26, PAD27, PAD28, PAD29, PAD30, PAD31, PAD32, PAD33, PAD34, PAD35, PAD36, PAD37: WIREPAD3,81/1,3; 3,81/1,3
X1: F37HP

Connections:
1: PAD1.1, X1.1
2: PAD2.1, X1.2
3: PAD3.1, X1.3
4: PAD4.1, X1.4
5: PAD5.1, X1.5
6: PAD6.1, X1.6
7: PAD7.1, X1.7
8: PAD8.1, X1.8
9: PAD9.1, X1.9
10: PAD10.1, X1.10
11: PAD11.1, X1.11
12: PAD12.1, X1.12
13: PAD13.1, X1.13
14: PAD14.1, X1.14
15: PAD15.1, X1.15
16: PAD16.1, X1.16
17: PAD17.1, X1.17
18: PAD18.1, X1.18
19: PAD19.1, X1.19
20: PAD20.1, X1.20
21: PAD21.1, X1.21
22: PAD22.1, X1.22
23: PAD23.1, X1.23
24: PAD24.1, X1.24
25: PAD25.1, X1.25
26: PAD26.1, X1.26
27: PAD27.1, X1.27
28: PAD28.1, X1.28
29: PAD29.1, X1.29
30: PAD30.1, X1.30
31: PAD31.1, X1.31
32: PAD32.1, X1.32
33: PAD33.1, X1.33
34: PAD34.1, X1.34
35: PAD35.1, X1.35
36: PAD36.1, X1.36
37: PAD37.1, X1.37


Board: 2 copper layers, 71.0 x 36.5 mm, 38 parts (0 on the bottom side), 37 nets.

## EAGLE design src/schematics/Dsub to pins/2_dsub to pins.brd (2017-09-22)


Board: 2 copper layers, 98.5 x 75.5 mm, 39 parts (0 on the bottom side), 37 nets.

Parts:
X1, X2, X3, X4, X5, X6, X7, X8, X9, X10, X11, X12, X13, X14, X15, X16, X17, X18, X19, X20, X21, X22, X23, X24, X25, X26, X27, X28, X29, X30, X31, X32, X33, X34, X35, X36, X37: 22-23-2021
X40: M37HP
X41: F37HP

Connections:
1: X1.1, X40.1, X41.1
2: X2.1, X40.2, X41.2
3: X3.1, X40.3, X41.3
4: X4.1, X40.4, X41.4
5: X5.1, X40.5, X41.5
6: X6.1, X40.6, X41.6
7: X7.1, X40.7, X41.7
8: X8.1, X40.8, X41.8
9: X9.1, X40.9, X41.9
10: X10.1, X40.10, X41.10
11: X11.1, X40.11, X41.11
12: X12.1, X40.12, X41.12
13: X13.1, X40.13, X41.13
14: X14.1, X40.14, X41.14
15: X15.1, X40.15, X41.15
16: X16.1, X40.16, X41.16
17: X17.1, X40.17, X41.17
18: X18.1, X40.18, X41.18
19: X19.1, X40.19, X41.19
20: X20.1, X40.20, X41.20
21: X21.1, X40.21, X41.21
22: X22.1, X40.22, X41.22
23: X23.1, X40.23, X41.23
24: X24.1, X40.24, X41.24
25: X25.1, X40.25, X41.25
26: X26.1, X40.26, X41.26
27: X27.1, X40.27, X41.27
28: X28.1, X40.28, X41.28
29: X29.1, X40.29, X41.29
30: X30.1, X40.30, X41.30
31: X31.1, X40.31, X41.31
32: X32.1, X40.32, X41.32
33: X33.1, X40.33, X41.33
34: X34.1, X40.34, X41.34
35: X35.1, X40.35, X41.35
36: X36.1, X40.36, X41.36
37: X37.1, X40.37, X41.37

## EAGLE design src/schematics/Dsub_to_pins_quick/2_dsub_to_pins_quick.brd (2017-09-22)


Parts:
JP1, JP2, JP3, JP5, JP6, JP7, JP8, JP9, JP10: PINHD-1X10; 1X10
JP4, JP11, JP12: PINHD-1X7; 1X07
X33: M37HP
X34: F37HP

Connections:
1: JP1.1, JP5.1, JP6.1, X33.1, X34.1
2: JP1.2, JP5.2, JP6.2, X33.2, X34.2
3: JP1.3, JP5.3, JP6.3, X33.3, X34.3
4: JP1.4, JP5.4, JP6.4, X33.4, X34.4
5: JP1.5, JP5.5, JP6.5, X33.5, X34.5
6: JP1.6, JP5.6, JP6.6, X33.6, X34.6
7: JP1.7, JP5.7, JP6.7, X33.7, X34.7
8: JP1.8, JP5.8, JP6.8, X33.8, X34.8
9: JP1.9, JP5.9, JP6.9, X33.9, X34.9
10: JP1.10, JP5.10, JP6.10, X33.10, X34.10
11: JP2.1, JP7.1, JP8.1, X33.11, X34.11
12: JP2.2, JP7.2, JP8.2, X33.12, X34.12
13: JP2.3, JP7.3, JP8.3, X33.13, X34.13
14: JP2.4, JP7.4, JP8.4, X33.14, X34.14
15: JP2.5, JP7.5, JP8.5, X33.15, X34.15
16: JP2.6, JP7.6, JP8.6, X33.16, X34.16
17: JP2.7, JP7.7, JP8.7, X33.17, X34.17
18: JP2.8, JP7.8, JP8.8, X33.18, X34.18
19: JP2.9, JP7.9, JP8.9, X33.19, X34.19
20: JP2.10, JP7.10, JP8.10, X33.20, X34.20
21: JP3.1, JP9.1, JP10.1, X33.21, X34.21
22: JP3.2, JP9.2, JP10.2, X33.22, X34.22
23: JP3.3, JP9.3, JP10.3, X33.23, X34.23
24: JP3.4, JP9.4, JP10.4, X33.24, X34.24
25: JP3.5, JP9.5, JP10.5, X33.25, X34.25
26: JP3.6, JP9.6, JP10.6, X33.26, X34.26
27: JP3.7, JP9.7, JP10.7, X33.27, X34.27
28: JP3.8, JP9.8, JP10.8, X33.28, X34.28
29: JP3.9, JP9.9, JP10.9, X33.29, X34.29
30: JP3.10, JP9.10, JP10.10, X33.30, X34.30
31: JP4.1, JP11.1, JP12.1, X33.31, X34.31
32: JP4.2, JP11.2, JP12.2, X33.32, X34.32
33: JP4.3, JP11.3, JP12.3, X33.33, X34.33
34: JP4.4, JP11.4, JP12.4, X33.34, X34.34
35: JP4.5, JP11.5, JP12.5, X33.35, X34.35
36: JP4.6, JP11.6, JP12.6, X33.36, X34.36
37: JP4.7, JP11.7, JP12.7, X33.37, X34.37

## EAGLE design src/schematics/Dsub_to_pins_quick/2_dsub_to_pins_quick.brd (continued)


Board: 2 copper layers, 70.1 x 63.2 mm, 14 parts (0 on the bottom side), 37 nets.

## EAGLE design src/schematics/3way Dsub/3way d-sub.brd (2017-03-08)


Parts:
X1: F37HP
X3, X4: M37HP

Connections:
1: X1.1, X3.1, X4.1
2: X1.2, X3.2, X4.2
3: X1.3, X3.3, X4.3
4: X1.4, X3.4, X4.4
5: X1.5, X3.5, X4.5
6: X1.6, X3.6, X4.6
7: X1.7, X3.7, X4.7
8: X1.8, X3.8, X4.8
9: X1.9, X3.9, X4.9
10: X1.10, X3.10, X4.10
11: X1.11, X3.11, X4.11
12: X1.12, X3.12, X4.12
13: X1.13, X3.13, X4.13
14: X1.14, X3.14, X4.14
15: X1.15, X3.15, X4.15
16: X1.16, X3.16, X4.16
17: X1.17, X3.17, X4.17
18: X1.18, X3.18, X4.18
19: X1.19, X3.19, X4.19
20: X1.20, X3.20, X4.20
21: X1.21, X3.21, X4.21
22: X1.22, X3.22, X4.22
23: X1.23, X3.23, X4.23
24: X1.24, X3.24, X4.24
25: X1.25, X3.25, X4.25
26: X1.26, X3.26, X4.26
27: X1.27, X3.27, X4.27
28: X1.28, X3.28, X4.28
29: X1.29, X3.29, X4.29
30: X1.30, X3.30, X4.30
31: X1.31, X3.31, X4.31
32: X1.32, X3.32, X4.32
33: X1.33, X3.33, X4.33
34: X1.34, X3.34, X4.34
35: X1.35, X3.35, X4.35
36: X1.36, X3.36, X4.36
37: X1.37, X3.37, X4.37


Board: 2 copper layers, 109.0 x 77.5 mm, 3 parts (0 on the bottom side), 37 nets.

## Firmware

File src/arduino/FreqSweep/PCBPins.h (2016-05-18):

/*Pin Numbering for PCB version - changed to reduce trace length */

// switch network pin definitions
const int DINp = 39;
const int DINn = 41;
const int SCLK = 43;
const int SYNC = 35;
const int RESET = 37;
const int TEST_1 = 33;
const int TEST_2 = 45;

// indicator pins
const int IND_SWITCH = 3;
const int IND_STIM = 4;
const int IND_START = 5;
const int IND_STOP = 6;
const int IND_FREQ = 9;

const int IND_EX_1 = 10;
const int IND_EX_2 = 11;
const int IND_EX_3 = 12;

//pins to turn the triggers on and off
const int TRIG_DISABLE_1 = 7;
const int TRIG_DISABLE_2 = 13;

//interupt pins
const int INTR_PMARK = 25; // pin to decect pmark - MUST BE AT POSITION 0 OF A DUE PORT 25 is 0 on portD - check http://arduino.cc/en/Hacking/PinMappingSAM3X
const int CS_EXTRA = 24; // bonus output pin on the CS side, not really used but whatever

//bonus pins
const int BONUS_1 = 47;
const int BONUS_2 = 49;
const int BONUS_3 = 51;
const int BONUS_4 = 53;

//Power Pins
const int PWR_STIM = 52;

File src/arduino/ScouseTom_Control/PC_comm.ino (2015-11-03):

void establishContact() {
	while (Serial.available() <= 0) {
		Serial.print('A');   // send a capital A
		delay(300);
	}
	char inb = Serial.read();
}

int PC_getsettings()
{
	/*
	read settings from PC in standard order:

	data types dont need to be different now as Due long and ints are the same (i think)
	but kept the same for ease of copy and pasting from Uno code :)

	number of injection - int
	number of electrodes - int
	number of frequencies - int
	number of repeated protcols - int

	ContactTime  uS - long - user sends ms
	Stimulator trigger time - us - user sends ms
	Stimulator trigger offset - us - - user sends ms
	Stimulator pulse width - long in uS - user sends us
	Stimulator wiper setting - int 8bit value
	Source channels[NumInj] - int
	Sink channels[NumInj] - int
	Freq[NumFreq] - long
	Amp[NumFreq] - long
	Measurementtime[NumFreq] - long - user sends ms
	check if comm fucked up after each one
	*/
	int commgoodness = 0; // flag for good communication
	int timeout = 0; // timeoutflag
	int tcurrent = 0; // current time var
	int tstart = millis(); //starting time

	int comminit = 0; // flag for starting thing

	Serial.print("<A>"); //send "im ready" byte

	//wait for response A from PC
	while (comminit == 0 && timeout == 0)
	{
		tcurrent = millis();
		if ((tcurrent - tstart) > (PC_timeoutlimit * 5)) // check if the timeout limit has been reached 5 times more than for a sinlge number
		{
			timeout = 1;
			comminit = 0;
			commgoodness = 0;
			//Serial.println("init timed out");
		}
		else
		{
			if (Serial.available() > 0) {
				byte c = Serial.read();
				//Serial.println(c);
				if (c == 'A') // if byte is A then we all good
				{
					comminit = 1;
					commgoodness = 1;
				}
			}
		}
	}
	if (comminit) // if comm was initialised....
	{
		int finished = 0; // stupid way of doing it but have this flag crack on
		while (finished == 0) // while loop so I can break the sequence after one bad comm
		{

			/*#####################################################
			Protocol and Experiment stuff
			#######################################################*/

			//get number of injections
			NumInj = getasciinum();
			sendasciinum(NumInj);
			if (NumInj == -1)
			{
				Serial.print("<NumInj Bad>");
				commgoodness = 0;
				break;
			}
			//get number of electrodes
			NumElec = getasciinum();
			sendasciinum(NumElec);
			if (NumElec == -1)
			{
				Serial.print("<NumElec Bad>");
				commgoodness = 0;
				break;
			}

			//obtain the number of boards used - if greater than 40 then 2 boards, if greater than 80 3 etc.

			NumBoard = NumElec / PinsPerBoard;
			if (NumElec % PinsPerBoard)
			{
				NumBoard++;
			}

			TotalPins = PinsPerBoard * NumBoard;



			//get number of frequencies
			NumFreq = getasciinum();
			sendasciinum(NumFreq);
			if (NumFreq == -1)
			{
				Serial.print("<NumFreq Bad>");
				commgoodness = 0;
				break;
			}

			if (NumFreq == 1)
			{
				SingleFreqMode = 1; // set flag high for single freq mode
				iFreq = 0; //set the counter to 0 (this should never change in SingleFreqMode!
			}
			else
			{
				SingleFreqMode = 0; //we are in multimode!
				iFreq = 0;  // doesnt need to be set here though...
			}

			//get number of repeats
			NumRep = getasciinum();
			sendasciinum(NumRep);
			if (NumRep == -1)
			{
				Serial.print("<NumRep Bad>");
				commgoodness = 0;
				break;
			}

			//set flag to use more consise front panel info
			if (NumInj > 999 || NumFreq > 999 || NumRep > 999)
			{
				LongDispWind = 1;
			}



			//get contact impedance measurement time
			ContactTime = getasciinum_long();
			sendasciinum_long(ContactTime);
			if (ContactTime == -1)
			{
				Serial.print("<ContactTime Bad>");
				commgoodness = 0;
				break;
			}

			ContactTime = ContactTime * 1000; //CONVERT INTO MICROSECONDS

			//get the compliance in mV
			Compliance = getasciinum_long();
			sendasciinum_long(Compliance);
			if (Compliance == -1)
			{
				Serial.print("<Compliance Bad>");
				Compliance = ComplianceDefault;
				commgoodness = 0;
				break;
			}



			/*#####################################################
			Stimulation stuff
			#######################################################*/

			//get stimulation trigger time
			StimTriggerTime = getasciinum_long();
			sendasciinum_long(StimTriggerTime);
			if (StimTriggerTime == -1)
			{
				Serial.print("<StimTriggerTime Bad>");
				commgoodness = 0;
				break;
			}
			StimTriggerTime = StimTriggerTime * 1000; //for compatibility user picks milliseconds, but microseconds used for more accuracy

			//get stimulation offset time
			StimOffset = getasciinum_long();
			sendasciinum_long(StimOffset);
			if (StimOffset == -1)
			{
				Serial.print("<StimOffset Bad>");
				commgoodness = 0;
				break;
			}

			StimOffset = StimOffset * 1000; //for compatibility user picks milliseconds, but microseconds used for more accuracy


			//get stimulation pulse width IN MICROSECONDS
			StimPulseWidth = getasciinum_long();
			sendasciinum_long(StimPulseWidth);
			if (StimPulseWidth == -1)
			{
				Serial.print("<StimPulseWidth Bad>");
				commgoodness = 0;
				break;
			}

			//get stimulation voltage wiper setting 
			StimWiperValue = getasciinum();
			sendasciinum(StimWiperValue);
			if (StimWiperValue == -1)
			{
				Serial.print("<StimTriggerTime Bad>");
				commgoodness = 0;
				break;
			}



			//Serial.println("Single things done");

			//check inputs for stim trigger time - all must be above 0 to use stim
			if (StimTriggerTime > 0 && StimOffset > 0 && StimPulseWidth > 0)
			{
				StimMode = 1; // StimMode is 1 - might need others for different stimulation types at some point
			}

			/*#####################################################
			ARRAY STUFF - PROTOCOL & FREQS & AMPS & MEASTIMES
			#######################################################*/

			int tmp_in = 0;

			//get sources
			for (int n = 0; n < NumInj; n++)
			{
				tmp_in = getasciinum();
				sendasciinum(tmp_in);
				if (tmp_in == -1)
				{
					Serial.print("<Source Bad>");
					commgoodness = 0;
					break;
				}
				Injection[n][0] = tmp_in;
			}

			if (tmp_in == -1)
			{
				Serial.print("<Source Bad>");
				commgoodness = 0;
				break;
			}

			//Serial.println("sourcesok");

			//get sinks
			for (int n = 0; n < NumInj; n++)
			{
				tmp_in = getasciinum();
				sendasciinum(tmp_in);
				if (tmp_in == -1)
				{
					Serial.print("<Sink Bad>");
					commgoodness = 0;
					break;
				}
				Injection[n][1] = tmp_in;
			}
			if (tmp_in == -1)
			{
				Serial.print("<Sink Bad>");
				commgoodness = 0;
				break;
			}

			//Serial.println("sinksok");

			//get frequencies
			for (int n = 0; n < NumFreq; n++)
			{
				tmp_in = getasciinum();
				sendasciinum(tmp_in);
				if (tmp_in == -1)
				{
					Serial.print("<Freq Bad>");
					commgoodness = 0;
					break;
				}
				Freq[n] = tmp_in;
			}
			if (tmp_in == -1)
			{
				Serial.print("<Freq Bad>");
				commgoodness = 0;
				break;
			}

			//Serial.println("freqsok");

			//get amplitudes
			for (int n = 0; n < NumFreq; n++)
			{
				tmp_in = getasciinum();
				sendasciinum(tmp_in);
				if (tmp_in == -1)
				{
					Serial.print("<Amp Bad>");
					commgoodness = 0;
					break;
				}
				Amp[n] = tmp_in;
			}
			if (tmp_in == -1)
			{
				Serial.print("<Amp Bad>");
				commgoodness = 0;
				break;
			}

			//Serial.println("ampsok");

			//get measurement times
			for (int n = 0; n < NumFreq; n++)
			{
				tmp_in = getasciinum_long();
				sendasciinum_long(tmp_in);
				if (tmp_in == -1)
				{
					Serial.print("<MeasTime Bad>");
					commgoodness = 0;
					break;
				}
				MeasTime[n] = tmp_in * 1000; // CONVERTED FROM MS TO US HERE
			}
			if (tmp_in == -1)
			{
				Serial.print("<MeasTime Bad>");
				commgoodness = 0;
				break;
			}

			//Serial.println("timessok");

			//get number of bad electrodes if any 

			NumBadElec = getasciinum();
			sendasciinum(NumBadElec);
			if (NumBadElec == -1)
			{
				Serial.print("<NumBadElec Bad>");
				commgoodness = 0;
				break;
			}

			//Serial.println("numbadok");

			// if there are bad electrodes then read array

			if (NumBadElec > 0)
			{
				for (int n = 0; n < NumBadElec; n++)
				{
					tmp_in = getasciinum();
					sendasciinum(tmp_in);
					if (tmp_in == -1)
					{
						Serial.print("<BadElec Bad>");
						commgoodness = 0;
						break;
					}
					BadElecs[n] = tmp_in;
				}
				if (tmp_in == -1)
				{
					Serial.print("<BadElec Bad>");
					commgoodness = 0;
					break;
				}
			}

			finished = 1;
		}

		//all ok so make the freq order vector

		for (int n = 0; n < NumFreq; n++)
		{
			FreqOrder[n] = n;
		}

	}
	return commgoodness;

}

//check inputs are ok and check writing to CS
int checkinputs()
{
	int inputok = 1;
	int inputgoodness = 1;
	int CSwritegoodness = 1;

	boolean finished = 0;
	while (finished == 0) //again stupid way of doing it
	{

		boolean compsetok = CS_SetCompliance(Compliance);

		if (!compsetok)
		{
			Serial.print("<CompSetErr>");
			inputok = 0;
			break;
		}

		if (StimMode) //is we are stimulating then check timings
		{
			if (StimOffset > MeasTime[0] || StimPulseWidth > StimTriggerTime) // stim offset must be less than measurement time and pulsewidth must be less than stimulation time 
			{
				Serial.print("<StimPulseTime>");
				inputok = 0;
				break;
				//Serial.println("stim bad");
			}

		}

		//send all settings to the current source to check that it likes them - this is so we dont check during multifreq mode and slow things down
		for (int i = 0; i < NumFreq; i++)
		{
			CSwritegoodness = CS_sendsettings_check(Amp[i], Freq[i]); //check each combination of amp and freq are sent ok to CS
			if (!CSwritegoodness)
			{
				Serial.print("<CSSetErr");
				Serial.print(i + 1);
				Serial.print(">");
				inputok = 0;
				break;
			}
		}

		//check that the reserved channels arent being addressed in protocol
		for (int curbrd = 0; curbrd < NumBoard; curbrd++)
		{
			//loop through each board
			int IllegalChannels[3] = { 38 + curbrd*PinsPerBoard, 39 + curbrd*PinsPerBoard, 40 + curbrd*PinsPerBoard }; //illegal channels for each board

			for (int curinj = 0; curinj < NumInj; curinj++) //loop through each injection
			{
				for (int i = 0; i < 3; i++) //loop through each illegal channel
				{
					/*Serial.print("Checking ");
					Serial.print(Injection[curinj][0]);
					Serial.print("and ");
					Serial.print(Injection[curinj][1]);

					Serial.print("against ");
					Serial.println(IllegalChannels[i]);*/
					
					//if sourced or sink through bad one then return error
					if (Injection[curinj][0] == IllegalChannels[i] || Injection[curinj][1] == IllegalChannels[i])
					{
						Serial.print("<IllegalChnProtLine");
						Serial.print(curinj+1);
						Serial.print(">");
						inputok = 0;
						break;
					}
				}
			}

		}



		finished = 1;

	}
	return inputok;

}
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

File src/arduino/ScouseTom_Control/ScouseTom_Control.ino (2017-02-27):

/*
Arduino Control Code for breadboard and PCB version - controlled by Matlab code (for now) ScouseTom_Init ScouseTom_Start etc.

Overview of commands is SOMEWHERE
########
To do:

Check that sources and sinks arent the same for a line in the protocol

Tidy up:
- everything under "do stuff" would be easier if it was replaced with inline functions - that way they could be jumped too in visual studio
- rearrange code into more logical tabs - the multifreq stuff within "CS_comm" for example
Debug mode - use #IF to set verbose debug mode

Pulse trains - so kirill can replicate thomas' experiments on nerve - repeated stim should demonstrate refactory period. Also could be used to replicate BOLD experimental paradigm - with

Lower power consumption - it is possible to set pmc_enable_sleep to save some power, or even put the SAM3X into "backup" mode, awakened by interupt on RX pin, but not sure how
also it is possible to turn off/lower clocks when not in use, and turn off adc's etc. my googling failed me. THis is unlikely to reduce the consumption by much however.
########

Jimmy wrote this so blame him

*/


//#####################################
// Libraries to include

#include <Wire.h> //i2c for digipot

//#include "BreadboardPins.h" // Pins for breadboard version - used by kirill and me (testing)
#include "PCBPins.h" // Pins for PCB version - these have been altered to more logical layout for PCB
#include "Stim.h" //Constants for stimulator things, with definitions of functions
#include "Switches.h" // Constants for switching channels
#include "CS_comm.h" // Constants used in serial communication with Current Source
#include "PC_comm.h" // Constants used in communicaltion with PC
#include "Pins.h" // constants used in indicator pins and reseting ALL pins to defaults etc.
#include "Errors.h" // error codes and warning messages
#include "Messages.h" // OK messages and other misc. things
#include "System_Control.h" //control constants - idle time definition etc.
#include "Injection.h" // injection defaults - max number of protocol lines etc.
#include "Compliance.h" // compliance check defaults and consts

/*############ CS Communications stuff - consts in CS_Comm.h ############*/

char CS_inputBuffer[CS_buffSize]; //char buffer to store output from current source
int CS_inputFinished = 0; //flag for complete response from current source
int LongDispWind = 0; // flag for if we have more than 3 digit length of repeats/freqs/prt so that we use the shorter text on the bottom window
char CS_outputBuffer[50]; // char array buffer for output strings to CS
int CS_commgoodness = 1; // flag for current communication goodness

/*############ PC Communications stuff - consts in PC_Comm.h ############*/

char PC_outputBuffer[50]; // char array buffer for output strings to PC
int PC_commgoodness = 1;
int PC_inputgoodness = 0;
/*############ Injection Stuff  - consts in Injection.h ############*/
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

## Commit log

2015-04-14 Added most of the old software and hardware, with very brief readmes. All in a state that would only make sense to current users.
    Also added new Controller software - latest version which has been used by kirill and jimmy so far - more testing needed
    [10 PORT HEADER.SLDPRT, 22-12-2044 Body.SLDPRT, 22-12-2044 Pin.SLDPRT, 22-12-2044.SLDASM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]
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2015-05-08 Complete Testing Arduino Code, fixed image relative paths
    [ScouseTom_New.brd, ScouseTom_New.sch]
2015-05-12 If this is a previous version of ScouseTom, but it's deprecated, it should not be in the latest version of the active most updated branch.
    [10 PORT HEADER.SLDPRT, 22-12-2044 Body.SLDPRT, 22-12-2044 Pin.SLDPRT, 22-12-2044.SLDASM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]
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2015-05-12 Move MatLab stuff from ScouseTom/ArduinoControl/Control to ScouseTom/src/matlab. Also, mat files are in resources/data, and txt files are in config/matlab.
    [ScouseTom_New.brd, ScouseTom_New.sch]
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2015-05-15 Started Case Design. Changed PCB pin PWR_SWTICH as used in serial1 on Due
    [ARDUINO DUE.SLDASM, Berg Header Receptacle 2.54 x 10 - FCI - 66951-010LF.sldprt, Berg Header Receptacle 2.54 x 36 - FCI - 66953-018LF.sldprt, Berg Header Recep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]
2015-05-18 Completed ScouseTom Case Design in SW2015. Reference Arduino Due modifyed from one on GrabCad. Stl included for printing
    [ARDUINO DUE.SLDASM, Berg Header Receptacle 2.54 x 10 - FCI - 66951-010LF.sldprt, Berg Header Receptacle 2.54 x 36 - FCI - 66953-018LF.sldprt, Berg Header Recep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]
2015-05-18 Updated Case Design so that it actually fits...
    [ScouseTomCasePrintLid.STL, ScouseTomCasePrintMain.STL, ScouseTom_Case-ScouseTom_Case_Body.SLDPRT, ScouseTom_Case-ScouseTom_Case_Lid.SLDPRT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]
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2015-05-27 Updated Case to provide extra room for cables and 37way DSUB on to for Biosemi
    [ScouseTomCasePrintLid.STL, ScouseTomCasePrintMain.STL, ScouseTom_Case-ScouseTom_Case_Body.SLDPRT, ScouseTom_Case-ScouseTom_Case_Lid.SLDPRT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]
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2015-05-29 Tom's Switch Network Design Files
    [Component Placement Data.csv, SWITCH NETWORK.DSN]
2015-05-29 Parllel CS Schematic and PCB Layout
    [top.brd, top.gbl, top.gbo, top.gbs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]
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2015-06-19 Moved Toms Schematics all into doc/schematics
    [Component Placement Data.csv, SWITCH NETWORK.DSN, ScouseTom_New.brd, ScouseTom_New.sch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]
2015-06-23 moved schematics from Doc to Source
    [Component Placement Data.csv, SWITCH NETWORK.DSN, ScouseTom_New.brd, ScouseTom_New.sch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]
2015-07-01 Added Tims ADC/AMP Schematicsm and updates to Shield - DRC left to do
    [ADC.brd, ADC.sch, Amp5.brd, Amp5.sch]
2015-07-01 gerber files and ignoring eagle backups
    [ScouseTom_New.GBL, ScouseTom_New.GBO, ScouseTom_New.GBS, ScouseTom_New.GTL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]
2015-07-01 Final version sent to PCBTrain with BOM and P&P
    [ScouseTom_New.GBL, ScouseTom_New.GBO, ScouseTom_New.GBS, ScouseTom_New.GTL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]
2015-07-07 Rerranged Toms Old Schematics, and Updates to Switching Board
    [Component Placement Data.csv, SWITCH NETWORK.DSN, SwitchBoard.brd, SwitchBoard.sch]
2015-07-07 Added Mak Connector for Silicon Elec to Schematics. Started routing Switchboard
    [SwitchBoard.brd, SwitchBoard.sch]
2015-07-09 SwNet - left hand side layout done
    [SwitchBoard.brd, SwitchBoard.sch]
2015-07-09 SwitchBoard Switches routed
    [SwitchBoard.brd, SwitchBoard.sch]
2015-07-16 Switch Board Layout finished, needs text and logo
    [ScouseTom_New_BOM.xlsx, SwitchBoard.brd, SwitchBoard.sch]
2015-07-20 SwitchNetwork Finished. Gerber/BOM/P&P generated
    [BOM_Example.xlsx, PCB-Train-free-components-list.xls, Pick_and_Place_Example.xlsx, ScouseTom_New_Pick_and_Place.xlsx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]
2015-07-20 Board Libraries Added
    [SwitchBoard_BOM.xlsx]
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2015-07-28 Started Debug Phantom with Dsub Connection
    [Debug_Phantom.brd, Debug_Phantom.sch]
2015-08-04 debug phantom before routing
    [Debug_Phantom.brd, Debug_Phantom.sch]
2015-08-05 Finished Debug Phantom and made gerber files sent to PCBTrain
    [Debug_Phantom.GBL, Debug_Phantom.GBO, Debug_Phantom.GBS, Debug_Phantom.GTL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]
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2015-08-21 minor schematic change i think from opening and closing
    [SwitchBoard.sch]
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2015-09-01 Minor clarification in text in shcematic
    [SwitchBoard.sch]
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2015-09-15 Updating Case design, Lid to be done
    [ScouseTom_Case.SLDASM, ScouseTom_Case.sldprt, ScouseTom_Shield.SLDPRT]
2015-09-17 Finished Initial Version of New Case Design
    [ScouseTomCasePrintLid.STL, ScouseTomCasePrintMain.STL, ScouseTom_Case-ScouseTom_Case_Body.SLDPRT, ScouseTom_Case-ScouseTom_Case_Lid.SLDPRT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]
2015-09-18 Case and Lid Design Finished with Text and Fasteners
    [ScouseTomCasePrintLid.STL, ScouseTom_Case-ScouseTom_Case_Body.SLDPRT, ScouseTom_Case-ScouseTom_Case_Lid.SLDPRT, ScouseTom_Case.SLDASM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]
2015-09-21 Finished Shield Case Design. Added Model of SwitchBoard
    [ScouseTomCasePrintLid.STL, ScouseTom_Case-ScouseTom_Case_Lid.SLDPRT, ScouseTom_Case.SLDASM, ScouseTom_Case.sldprt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]
2015-09-21 Started Switchboard Case. Added EAGLE CAD settings to doc for future ref
    [ScouseTom_Case-ScouseTom_Case_Body.SLDPRT, ScouseTom_Case.SLDASM, ScouseTom_SwitchBoard_Case.SLDASM, SwitchBoardCase - Lid.sldprt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]
2015-09-22 Finished SwitchBoard Case and Lid
    [SwitchBoard.brd, SwitchBoardCase - Lid.STL, SwitchBoardCase - Lid.sldprt, SwitchBoardCase.sldprt]
2015-09-23 Moved Switch Position and resized based on actual thing not spec sheet
    [ScouseTom_SwitchBoard_Case.SLDASM, Switch.SLDPRT, SwitchBoardCase - Main.sldprt, SwitchBoardCase.sldprt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]
2015-09-23 updated switchboard with proper daisy chain select and test 1 correct wiring
    [SwitchBoard.GBL, SwitchBoard.GBO, SwitchBoard.GBS, SwitchBoard.GTL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]
2015-09-24 minor changes to board before sending to PCBTrain
    [SwitchBoard.GBL, SwitchBoard.GBS, SwitchBoard.GTL, SwitchBoard.GTS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]
2015-09-25 Added Dsub Cover Final, Fixed bug in Contact Check Compliance - Now references the *contact check* rprotocol in calc
    [DsubCover.SLDPRT, DsubCover.STL]
2015-09-29 Finished DsubCover
    [DsubCover.SLDPRT, DsubCover.STL]
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2015-10-26 Minor Changes to BOM and Case
    [ScouseTom_Case.SLDASM, ScouseTom_SwitchBoard_Case.SLDASM, SwitchBoard_BOM.xlsx]
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2015-11-05 Corrected part no for Micro USB on switch network
    [BOM_Example.xlsx, SwitchBoard_BOM.xlsx]
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2016-03-01 Updated ScouseTom Shield SilkScreen and Gerber for PCB train order
    [ScouseTom_New.GBL, ScouseTom_New.GBO, ScouseTom_New.GBS, ScouseTom_New.GTL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]
2016-03-01 Changed USB connector on SwitchBoard
    [SwitchBoard.brd, SwitchBoard.sch]
2016-03-01 Minor Silkscreen updates to SwitchBoard. New Gerber files and updated BOM and P&P with lipo connector
    [SwitchBoard.GBL, SwitchBoard.GBO, SwitchBoard.GBS, SwitchBoard.GTL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]
2016-03-01 Files ready to send to PCBTrain
    [SwitchBoard.brd]
2016-03-01 cleared up gerber dir
    [SwitchBoard.brd]
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2016-03-04 Added calculation of number of parts needed to order. I hate excel
    [FarnellOrder.xlsx, ScouseTom_New_BOM.xlsx, SwitchBoard_BOM.xlsx]
2016-03-14 updated Farnell order spreadsheet
    [FarnellOrder.xlsx]
2016-03-14 fixed gerber files, previosuly had top silk on the bottom silk aswell
    [ScouseTom_New.GBO]
2016-04-04 Added Figures for Components to docs, for use in documentation
    [ScouseTom_New.dwg, ScouseTom_New.dxf, SwitchBoard.brd, SwitchBoard.dwg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]
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2016-05-24 updated BOM to reflect correct R10, thanks to weilong
    [SwitchBoard_BOM.xlsx]
2016-07-04 Files for actichamp connector holder
    [connector_base_A.SLDPRT, connector_base_B.SLDPRT, support.SLDPRT]
2016-11-03 Resistor Phantom
    [Resistor_Phantom.brd, Resistor_Phantom.sch]
2016-11-08 Resistor Phantom v1
    [Resistor_Phantom.GBL, Resistor_Phantom.GBO, Resistor_Phantom.GBS, Resistor_Phantom.GKO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]
2017-01-03 Added Dsub to croc connector, gerbers sent to PCBway
    [dsub_to_pins.GBL, dsub_to_pins.GBO, dsub_to_pins.GBS, dsub_to_pins.GTL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]
2017-01-26 started output impedance tester
    [OutputZTester.brd, OutputZTester.sch]
2017-02-07 Reorganised schematics folder. Added more documentation
    [ADC.brd, ADC.sch, Amp5.brd, Amp5.sch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]
2017-02-20 Finished sim of TIA and Droop circuit. Started PCB
    [OutputZTester.brd, OutputZTester.sch]
2017-02-20 Basic layout for both circuits done
    [OutputZTester.brd, OutputZTester.sch]
2017-02-21 one mo' 'gin
    [OutputZTester.brd, OutputZTester.sch]
2017-02-21 finished layout and board for z check
    [OutputZTester.brd, OutputZTester.sch]
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2017-08-01 Fixed typos
    [SwitchBoard_Pick_and_Place.xlsx]
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2017-11-23 Dsub box, fixed trace on debug phantom. Gerber and CAM data for pcbway
    [Actichamp_box_Side.SLDPRT, Actichamp_box_back.SLDPRT, Actichamp_box_base.SLDPRT, Actichamp_simple_box.SLDASM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]
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2018-01-30 CS extra pin added. Fixed angles on tracks
    [ScouseTom_New.brd, ScouseTom_New.sch]
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2018-02-08 Updated Switchboard - pull down resistors, fixed routing, protection diodes and different battery connector
    [ScouseTom_New.brd, SwitchBoard.GBL, SwitchBoard.GBO, SwitchBoard.GBS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]
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2019-03-26 fixed error in BOM
    [SwitchBoard_BOM.xlsx]
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

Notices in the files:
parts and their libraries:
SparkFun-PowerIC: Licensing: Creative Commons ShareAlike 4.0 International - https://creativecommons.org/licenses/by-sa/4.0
